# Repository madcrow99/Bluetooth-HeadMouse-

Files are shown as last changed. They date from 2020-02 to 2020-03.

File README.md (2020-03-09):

# Bluetooth-HeadMouse-
Control mouse over Bluetooth with head movement. 

This project uses a RN-42 Bluetooth module (version 6.03 or later) to send HID (mouse pointer and button commands) reports to computer or phone. Mouse movements are related to the movement of an MPU6050 (gyroscope) placed on the side of the users head (e.g. respirator mask, headband, hat, eye glasses earpiece...). This has been tested on Android, Windows and Ubuntu.

Connect Arduino MEGA, RN-42 (use one module for each device) , 4 buttons and the MPU6050 as outlined in HeadMouse.fzz.

Run HID_Config.ino, to configure the rn-42. This sets the RN-42 to the combo(mouse and keyboard ) profile.

Pair RN-42 modules with devices (phone and computer). This step is simply pairing a Bluetooth device from the phone or computer.

Upload headMouse.ino

If the pointer moves while the MPU 6050 is stationary, run calibrate_gyro.ino with MPU6050 stationary. Update values of averageX and averageZ in headMouse.ino.

Included are step and stl files for power wheelchair button mounts (left and right, hand and head). 

Headrest
Powerchair

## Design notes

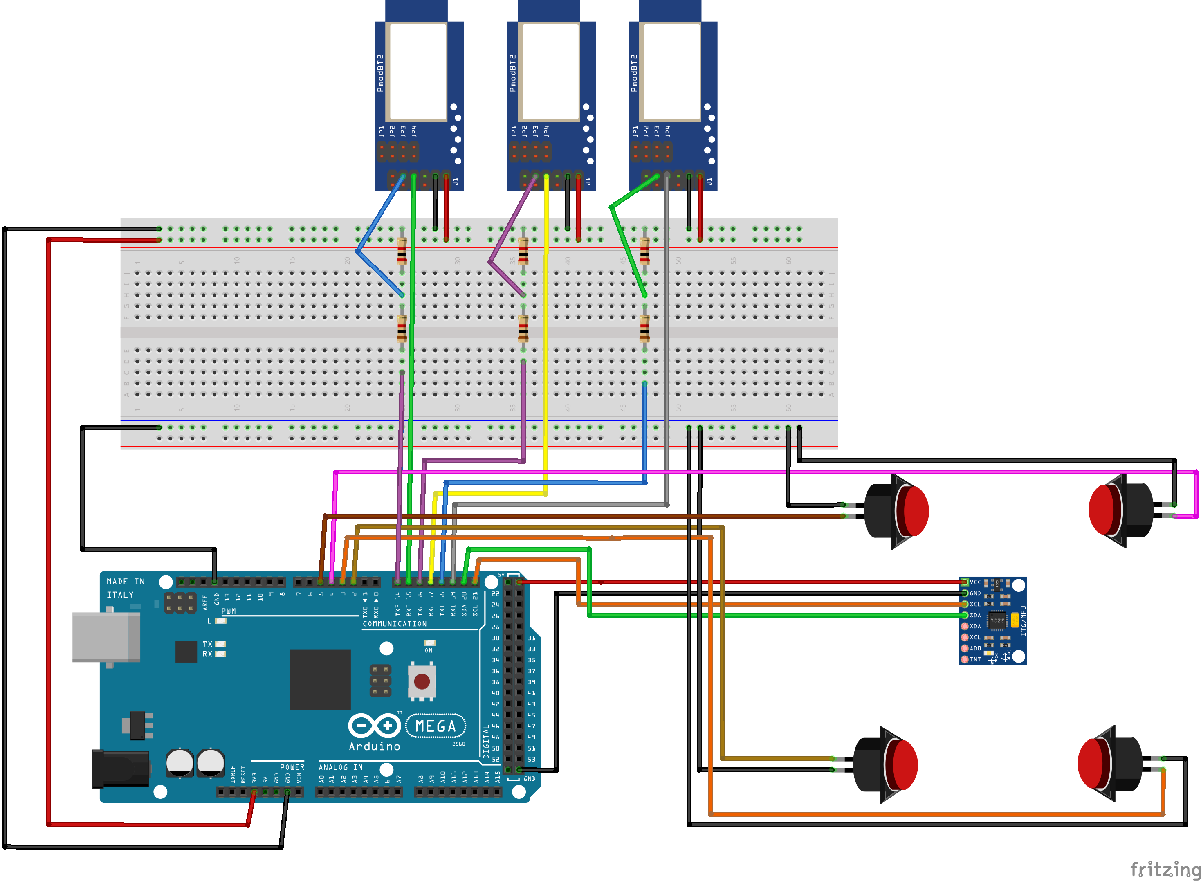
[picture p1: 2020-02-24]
HeadMouse_bb.png

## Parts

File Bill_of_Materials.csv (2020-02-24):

Item | Description | Manufacturer | Part Number | QTY | Unit Cost | Cost | Digikey Link | Unit Cost | Cost | Alternate Link
1 | Inertial Movement Sensor | SparkFun Electronics | SEN-11028 | 1 | $42.83 | $42.83 | https://www.digikey.ca/products/en?keywords=SEN-11028 | $29.95 | $29.95 | https://www.sparkfun.com/products/11028
2 | Arduino Mega | Arduino | A000067 | 1 | $55.05 | $55.05 | https://www.digikey.ca/products/en/development-boards-kits-programmers/evaluation-boards-embedded-mcu-dsp/786 | $38.95 | $38.95 | https://www.sparkfun.com/products/11061
3 | Bluetooth Module | SparkFun Electronics | WRL-12576 | 3 | $39.97 | $119.91 | https://www.digikey.ca/products/en?KeyWords=WRL-12576 | $27.95 | $83.85 | https://www.sparkfun.com/products/12576
 |  |  |  |  |  | $217.79 |  |  | $152.75

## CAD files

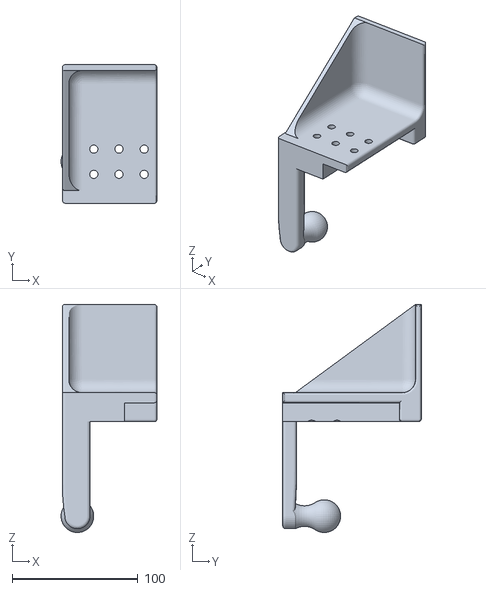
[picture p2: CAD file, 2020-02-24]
Hand Button and Ball Mount Right.stl
76.1 x 110.0 x 181.0

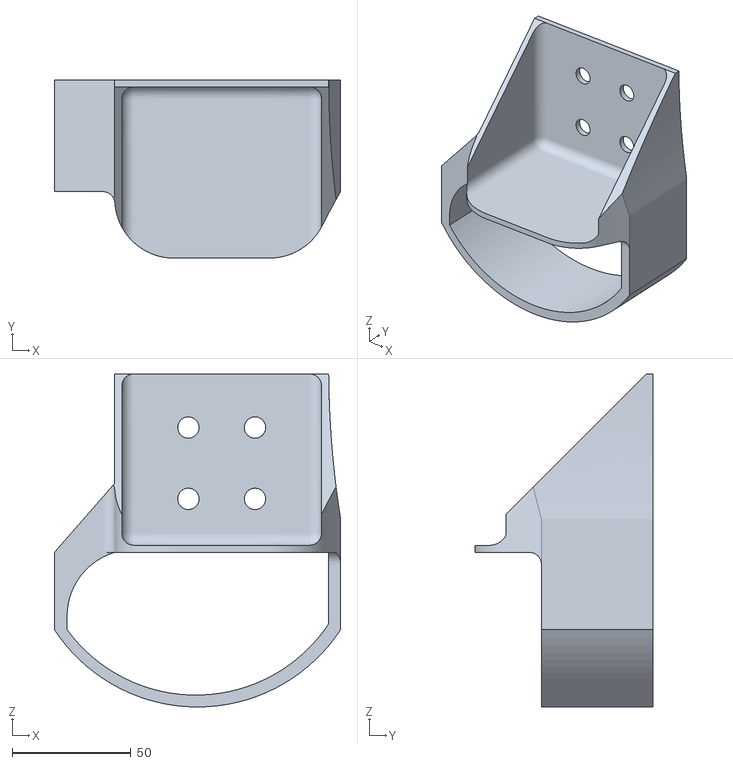
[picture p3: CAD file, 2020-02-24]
Hand Button Mount Left.stl
120.3 x 75.0 x 140.0

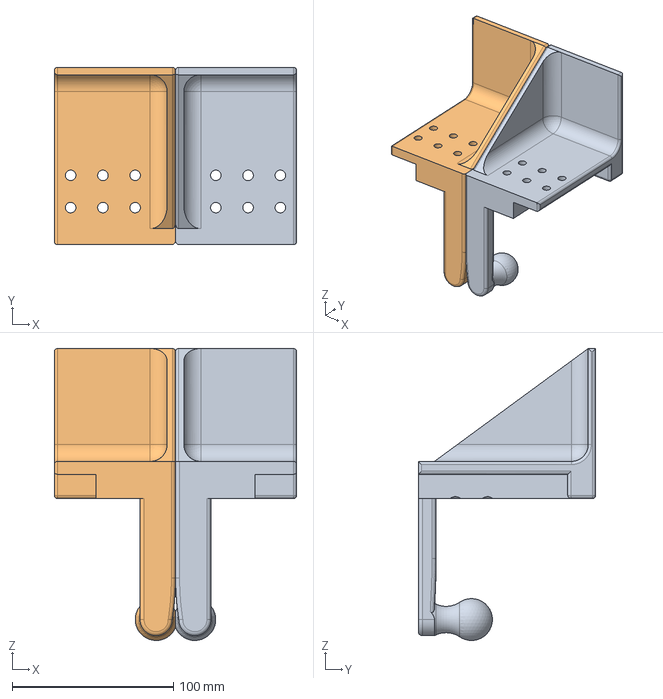
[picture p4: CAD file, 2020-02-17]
Hand Button and Ball Mount.step
150.3 x 110.0 x 181.0 mm

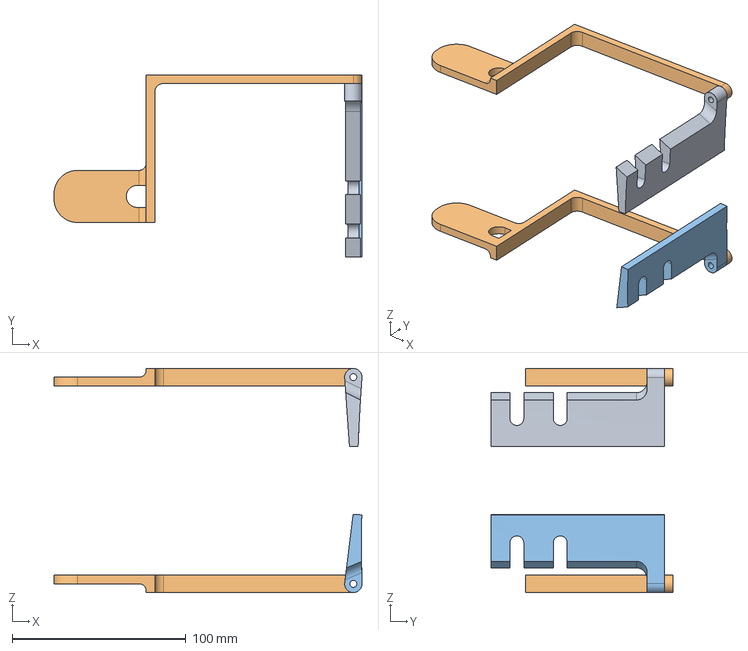
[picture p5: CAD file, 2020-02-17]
Head Button Mount.step
177.2 x 105.0 x 129.0 mm

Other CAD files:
Hand Button Mount Right.stl
Hand Button and Ball Mount Left.stl
Head Button Mount.stl

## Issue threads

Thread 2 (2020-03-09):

### ISSUE TITLE
Apple iOS should now work..

### ISSUE THREAD

**Issue by willwade** [madcrow99/Bluetooth-HeadMouse-#2]
Cool project. Just a FYI your readme says Apple iOS devices wont work - they will now under iOS 13

Interesting you are using a mega and the rn-42. We are finding that the nrf52840 is a lot more reliable to work with - and using something like https://www.adafruit.com/product/4516 - may make the whole thing a lot smaller. I see why you have three bluetooth modules - to use on different devices. Thats one thing from reading the docs that the nrf52840 should be able to do. One idea is to just change the name of the BT device and toggle between three names -although I have to admit - I haven't worked it out yet!

Great stuff. Will add to https://openassistive.org

NB: Add a licence - https://choosealicense.com - it will make forks and future work on this a bit easier :)

**Comment by madcrow99** [comment]
Thanks for the information!

I used the mega for the 3 serial UART. I also use it for drive controls for
my chair so the mega is good for lots of pins.

I agree with you on the nrf. I actually made a head mouse this week with an
adafruit feather sense. It was so much easier as everything needed came
included on the board. Plus their examples and libraries are incredible.
BLE is nice too.

Mike

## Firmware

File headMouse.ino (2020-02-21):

#include <Bounce2.h>
#include <Wire.h>
#include <I2Cdev.h>
#include <MPU6050.h>


MPU6050 mpu;
int16_t ax, ay, az, gx, gy, gz;
int vx, vy;


int averageCount = 0;
double averageX = -20;//from calibrate_gyro.ino
double averageY = 0;
double averageZ = 52;//from calibrate_gyro.ino

#define NUM_BUTTONS 4
int BUTTON_PINS[NUM_BUTTONS] = { 2, 3, 4, 5};

Bounce * buttons = new Bounce[NUM_BUTTONS];

int buttonState = 0;
int device = 2;

bool lastButton1 = false;
bool lastButton2 = false;

long buttonTimer = 0;
long phoneTimer = 0;

long longPressTime = 500;
long phonePressTime = 1000;

boolean buttonActive = false;
boolean longPressActive = false;
boolean longPress2Active = false;

boolean phoneActive = false;
boolean phoneActiveLong = false;
boolean button0Active = false;
boolean button2Active = false;
boolean RButton2 = false;


signed int dx = -127;
signed int dy = 40;

void setup() {
  Serial.begin(115200);
  Serial1.begin(115200);
  Serial2.begin(115200);
  Serial3.begin(115200);

  Wire.begin();
  mpu.initialize();
  if (!mpu.testConnection()) {
    while (1);
  }
  
  for (int i = 0; i < NUM_BUTTONS; i++) {
    buttons[i].attach( BUTTON_PINS[i] , INPUT_PULLUP  );       //setup the bounce instance for the current button
    buttons[i].interval(30);              // interval in ms
  }


}

void loop() {

  for (int i = 0; i < NUM_BUTTONS; i++)  {
    // Update the Bounce instance :
    buttons[i].update();
  }

  //Computer one computer two or phone
  //long press button 4 to switch between devices
  if ( buttons[2].read() == HIGH && buttons[3].read() == LOW &&
       buttons[0].read() == HIGH && buttons[1].read() == HIGH ) {

    if (phoneActive == false) {

      phoneActive = true;
      phoneTimer = millis();

    }

    if ((millis() - phoneTimer > phonePressTime) ) {
      phoneActiveLong = true;

    }
  }

  if ( buttons[2].read() == HIGH && buttons[3].read() == HIGH &&
       buttons[0].read() == HIGH && buttons[1].read() == HIGH &&  phoneActiveLong == true) {
        
    phoneActive = false;
    phoneActiveLong = false;
    device ++;
    if (device > 3) device = 1;
    
  }

  if ( buttons[3].read() == HIGH ) {
    if (device == 1) comp1();
    if (device == 2) phone();
    if (device == 3) comp2();
  }

}

//using two buttons (0,1,2)
//0 is use to jump the pointer horzontally with a short press (alternating direction)
//0 is use to jump the pointer vertically with a long press (alternating direction)
//It is used to limit the amount of head movement required

//1 is the left mouse button

//0 and 1 pressed together is the right mouse button

//2 is scroll. short press down. long press up.

void comp1() {
 
  mpu.getMotion6(&ax, &ay, &az, &gx, &gy, &gz);

  vx = -((gx - averageX) / 200);//change value as needed for mouse sensitivity
  vy = ((gz - averageZ) / 200);//change value as needed for mouse sensitivity


 mouseMove1(vx, vy, buttonState,0);

  if ( buttons[1].read() == LOW && lastButton1 == false) {

    lastButton1 = true;
    buttonState = 1;//left mouse down click
  }

  if ( buttons[1].read() == HIGH && lastButton1 == true) {

    lastButton1 = false;
    buttonState = 0;//buttons released
  }


  if ( buttons[0].read() == LOW &&  buttons[1].read() == LOW &&  RButton2 == false) {
    RButton2 = true;
    buttonState = 2;//right mouse down click
    button0Active = false;
  }


  if ( buttons[0].read() == HIGH &&  buttons[1].read() == HIGH && RButton2 == true) {

    RButton2 = false;
    buttonState = 0;
  }
  
  if ( buttons[0].read() == LOW &&  buttons[1].read() == HIGH && RButton2 == false) {


    if (button0Active == false) {

      button0Active = true;
      buttonTimer = millis();

    }

    if ((millis() - buttonTimer > longPressTime)) {


      mouseMove1(0, dy, 0, 0);
      longPressActive = true;
    }
  }
  else  if (buttons[0].read() == HIGH ) {

    if (button0Active == true) {

      if (longPressActive == true) {

        longPressActive = false;
        dy = dy * -1;

      } else {
        for (int i = 0; i < 5; i++)  {
          mouseMove1(dx, 0, 0, 0);
        }

      }

      dx = dx * -1;

      button0Active = false;
    }
  }


  if ( buttons[2].read() == LOW) {


    if (button2Active == false) {

      button2Active = true;
      buttonTimer = millis();

    }

    if ((millis() - buttonTimer > longPressTime) ) {
      mouseMove1(0, 0, buttonState, 1);

      delay(85);
      longPress2Active = true;
    }

  }
  else  if (buttons[2].read() == HIGH ) {

    if (button2Active == true) {

      if (longPress2Active == true) {

        longPress2Active = false;

      } else {

        mouseMove1(0, 0, buttonState, -5);
        delay(85);

      }

      button2Active = false;

    }

  }

  

}

//using three buttons (0,1,2)
//0 is use to jump the pointer horzontally with a short press (alternating direction)
//0 is use to jump the pointer vertically with a long press (alternating direction)
//It is used to limit the amount of head movement required

//1 is the left mouse button (similar to a tap or swipe)

//2 is to scroll. short press down. long press up. Certain apps do not respond to the left click swipe (e.g. google chrome)
void phone() {


  mpu.getMotion6(&ax, &ay, &az, &gx, &gy, &gz);

  vx = -((gx - averageX) / 200);//change value as needed for mouse sensitivity
  vy = ((gz - averageZ) / 200);//change value as needed for mouse sensitivity


  mouseMove2(vx, vy, buttonState, 0);

  if ( buttons[1].read() == LOW && lastButton1 == false) {
  
    lastButton1 = true;
    buttonState = 1;
  }

  if (  buttons[1].read() == HIGH && lastButton1 == true) {
   
    lastButton1 = false;
    buttonState = 0;
  }


  if ( buttons[0].read() == LOW ) {


    if (button0Active == false) {

      button0Active = true;
      buttonTimer = millis();

    }
    if ((millis() - buttonTimer > longPressTime)) {

      mouseMove2(0, dy, buttonState, 0);

      longPressActive = true;
    }
  }
  else  if (buttons[0].read() == HIGH ) {

    if (button0Active == true) {

      if (longPressActive == true) {

        longPressActive = false;
        dy = dy * -1;

      } else {


        for (int i = 0; i < 5; i++)  {
          mouseMove2(dx, 0, buttonState, 0);
        }

      }

      dx = dx * -1;

      button0Active = false;
    }


  }

  if ( buttons[2].read() == LOW) {


    if (button2Active == false) {

      button2Active = true;
      buttonTimer = millis();

    }

    if ((millis() - buttonTimer > longPressTime) ) {
      mouseMove2(0, 0, buttonState, 1);

      delay(85);
      longPress2Active = true;
    }

  }
  else  if (buttons[2].read() == HIGH ) {

    if (button2Active == true) {

      if (longPress2Active == true) {

        longPress2Active = false;

      } else {

        mouseMove2(0, 0, buttonState, -5);
        delay(85);

      }

      button2Active = false;

    }

  }

}



//using two buttons (0,1,2)
//0 is use to jump the pointer horzontally with a short press (alternating direction)
//0 is use to jump the pointer vertically with a long press (alternating direction)
//It is used to limit the amount of head movement required

//1 is the left mouse button

//0 and 1 pressed together is the right mouse button

//2 is scroll. short press down. long press up.

void comp2() {
 
  mpu.getMotion6(&ax, &ay, &az, &gx, &gy, &gz);

  vx = -((gx - averageX) / 125);//change value as needed for mouse sensitivity
  vy = ((gz - averageZ) / 125);//change value as needed for mouse sensitivity


 mouseMove3(vx, vy, buttonState,0);

  if ( buttons[1].read() == LOW && lastButton1 == false) {

    lastButton1 = true;
    buttonState = 1;//left mouse down click
  }

  if ( buttons[1].read() == HIGH && lastButton1 == true) {
    //if (  digitalRead(BUTTON_PINS[1]) == HIGH && lastButton1 == true) {

    lastButton1 = false;
    buttonState = 0;//buttons released
  }


  if ( buttons[0].read() == LOW &&  buttons[1].read() == LOW &&  RButton2 == false) {
    RButton2 = true;
    buttonState = 2;//right mouse down click
    button0Active = false;
  }


  if ( buttons[0].read() == HIGH &&  buttons[1].read() == HIGH && RButton2 == true) {

    RButton2 = false;
    buttonState = 0;
  }
  
  if ( buttons[0].read() == LOW &&  buttons[1].read() == HIGH && RButton2 == false) {


    if (button0Active == false) {

      button0Active = true;
      buttonTimer = millis();

    }

    if ((millis() - buttonTimer > longPressTime)) {


      mouseMove3(0, dy, 0, 0);
      longPressActive = true;
    }
  }
  else  if (buttons[0].read() == HIGH ) {

    if (button0Active == true) {

      if (longPressActive == true) {

        longPressActive = false;
        dy = dy * -1;

      } else {
        for (int i = 0; i < 5; i++)  {
          mouseMove3(dx, 0, 0, 0);
        }

      }

      dx = dx * -1;

      button0Active = false;
    }
  }


  if ( buttons[2].read() == LOW) {


    if (button2Active == false) {

      button2Active = true;
      buttonTimer = millis();

    }

    if ((millis() - buttonTimer > longPressTime) ) {
      mouseMove3(0, 0, buttonState, 1);

      delay(85);
      longPress2Active = true;
    }

  }
  else  if (buttons[2].read() == HIGH ) {

    if (button2Active == true) {

      if (longPress2Active == true) {

        longPress2Active = false;

      } else {

        mouseMove3(0, 0, buttonState, -5);
        delay(85);

      }

      button2Active = false;

    }

  }

  

}




void mouseMove3(int dx, int dy, int bttn, int scroll) {
  Serial3.write((byte)0xFD); //Start HID Report
  Serial3.write((byte)0x5); //Length byte
  Serial3.write((byte)0x2); //Descriptor byte
  Serial3.write(bttn);
  Serial3.write(dx);
  Serial3.write(dy);
  Serial3.write(scroll);

  delay(15);
}

void mouseMove1(int dx, int dy, int bttn, int scroll) {
  Serial1.write((byte)0xFD); //Start HID Report
  Serial1.write((byte)0x5); //Length byte
  Serial1.write((byte)0x2); //Descriptor byte
  Serial1.write(bttn);
  Serial1.write(dx);
  Serial1.write(dy);
  Serial1.write(scroll);

  delay(15);
}

void mouseMove2(int dx, int dy, int bttn, int scroll) {
  Serial2.write((byte)0xFD); //Start HID Report
  Serial2.write((byte)0x5); //Length byte
  Serial2.write((byte)0x2); //Descriptor byte
  Serial2.write(bttn);
  Serial2.write(dx);
  Serial2.write(dy);
  Serial2.write(scroll);

  delay(15);
}

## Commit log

2020-02-24 Add draft BOM
    [Bill_of_Materials.csv]
2020-02-24 Updated Fritzing diagram
    Edited Fritzing diagram to improve readibility and added image.
    [HeadMouse.fzz]
